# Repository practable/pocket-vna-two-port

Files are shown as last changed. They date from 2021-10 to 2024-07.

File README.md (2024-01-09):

# pocket-vna-two-port

A golang-based web service for the pocketvna.com](https://pocketvna.com/) vector network analyser, with an automated two-port calibration facility provided by additional RF hardware, for use with the open-source [practable.io](https://practable.io] remote lab ecosystem. The user interface is similar to [this](https://github.com/dpreid/pidui), although not yet publically released by the developer (coming soon!)

Status: Prototype has passed measurement quality check, and firmware has been updated to two-ports.

## API

Note that the optional "id" parameter does not affect the command itself, and is provided to help associate replies with the commands that produced them (in case responses come out of order)

### Reasonable range 

```
{"id":"rr","cmd":"rr"}
```
Response:
```
{"id":"rr","t":0,"cmd":"rr","range":{"start":500000,"end":4000000000}}
```

### Calibration

To Perform a full 2-port calibration issue a command like this:

```
{"id":"rcal","t":0,"cmd":"rc","range":{"start":1000000,"end":4000000000},"size":501,"islog":false,"avg":1}
```

501 points is quite slow, so for quick checking functionality, try fewer points.
```
{"id":"rcal","t":0,"cmd":"rc","range":{"start":1000000,"end":4000000000},"size":5,"islog":false,"avg":1}
```

 The `range`, `size`, `isLog` and `avg` are the same as before. This example uses the largest scan size possible (501 points)

### Measurement

These are all the measurements that can be taken (as before, they use the size, and range parameters from the cal):

```
{"id":"short","t":0,"cmd":"crq","what":"short","avg":1,"sparam":{"s11":true,"s12":true, "s21":true,"s22":true}}
{"id":"open","t":0,"cmd":"crq","what":"open","avg":1,"sparam":{"s11":true,"s12":true,"s21":true,"s22":true}}
{"id":"load","t":0,"cmd":"crq","what":"load","avg":1,"sparam":{"s11":true,"s12":true,"s21":true,"s22":true}}
{"id":"thru","t":0,"cmd":"crq","what":"thru","avg":1,"sparam":{"s11":true,"s12":true,"s21":true,"s22":true}}
{"id":"dut1","t":0,"cmd":"crq","what":"dut1","avg":1,"sparam":{"s11":true,"s12":true,"s21":true,"s22":true}}
{"id":"dut2","t":0,"cmd":"crq","what":"dut2","avg":1,"sparam":{"s11":true,"s12":true,"s21":true,"s22":true}}
{"id":"dut3","t":0,"cmd":"crq","what":"dut3","avg":1,"sparam":{"s11":true,"s12":true,"s21":true,"s22":true}}
{"id":"dut4","t":0,"cmd":"crq","what":"dut4","avg":1,"sparam":{"s11":true,"s12":true,"s21":true,"s22":true}} 
```

### Step wise calibration

New feature added to support students learning about the cal process

SC Command (Setup cal, sets the frequency range, number of points, distribution type, and averaging count)
`{"cmd":"sc","range":{"start":1000000,"end":4000000000},"size":20,"islog":false,"avg":1}`

SC Response
```
{"message":"ok","Command":{"id":"","t":0,"cmd":"sc","range":{"start":1000000,"end":4000000000},"size":20,"islog":false,"avg":1,"sparam":{"s11":false,"s12":false,"s21":false,"s22":false},"result":null,"what":"thru"}}
```

MC Short Command:
`{"cmd":"mc","what":"short"}`

MC Short Response (has no data):
```
{"message":"ok","Command":{"id":"","t":0,"cmd":"mc","range":{"start":0,"end":0},"size":0,"islog":false,"avg":0,"sparam":{"s11":false,"s12":false,"s21":false,"s22":false},"result":null,"what":"short"}}
```

MC Open Command:
`{"cmd":"mc","what":"open"}`

MC Open Response (has no data):
```
{"message":"ok","Command":{"id":"","t":0,"cmd":"mc","range":{"start":0,"end":0},"size":0,"islog":false,"avg":0,"sparam":{"s11":false,"s12":false,"s21":false,"s22":false},"result":null,"what":"open"}}
```

MC Load Command:
`{"cmd":"mc","what":"load"}`

MC Load Response (has no data):
```
{"message":"ok","Command":{"id":"","t":0,"cmd":"mc","range":{"start":0,"end":0},"size":0,"islog":false,"avg":0,"sparam":{"s11":false,"s12":false,"s21":false,"s22":false},"result":null,"what":"load"}}
```

MC Thru Command:

`{"cmd":"mc","what":"thru"}`

MC Thru Response (has no data):

```
{"message":"ok","Command":{"id":"","t":0,"cmd":"mc","range":{"start":0,"end":0},"size":0,"islog":false,"avg":0,"sparam":{"s11":false,"s12":false,"s21":false,"s22":false},"result":null,"what":"thru"}}
```

CC Command (cal confirm):

`{"cmd":"cc"}`

CC Command (has data, "what" indicates this is data for the thru with cal applied)
```
{"id":"","t":0,"cmd":"cc","range":{"start":0,"end":0},"size":0,"islog":false,"avg":0,"sparam":{"s11":false,"s12":false,"s21":false,"s22":false},"result":[{"s11":{"real":6.798285684431499e-16,"imag":2.4445757591977986e-15},"s12":{"real":1.0000000000000038,"imag":3.961372257700955e-15},"s21":{"real":0.9999999999999997,"imag":-2.5403542658420376e-15},"s22":{"real":-1.3100837207899224e-16,"imag":1.006857580582699e-15},"freq":1000000},{"s11":{"real":-5.4796192872464335e-18,"imag":3.681361022427108e-16},"s12":{"real":0.9999999999999998,"imag":1.291216167493111e-16},"s21":{"real":0.9999999999999998,"imag":1.0329729339944889e-16},"s22":{"real":-5.483483876630498e-16,"imag":2.274972688902102e-16},"freq":211473684},{"s11":{"real":4.935662660074536e-16,"imag":-7.96132869667085e-17},"s12":{"real":1.0000000000000002,"imag":9.417544964280893e-18},"s21":{"real":1,"imag":3.3389477600632256e-17},"s22":{"real":-5.493611090297354e-17,"imag":2.7110250401774997e-17},"freq":421947368},{"s11":{"real":-3.7997788415861466e-16,"imag":-5.874815142871674e-16},"s12":{"real":0.9999999999999998,"imag":-1.3589387524604561e-17},"s21":{"real":1,"imag":1.358938752460456e-16},"s22":{"real":2.7701351888980784e-16,"imag":2.4761558453947516e-16},"freq":632421052},{"s11":{"real":-1.770339245638541e-16,"imag":1.9778244425109326e-16},"s12":{"real":1,"imag":-8.300789127383292e-17},"s21":{"real":1,"imag":-1.3834648545638821e-17},"s22":{"real":1.8971165707760076e-16,"imag":2.4057070110192795e-16},"freq":842894736},{"s11":{"real":-4.2721621505142654e-16,"imag":-3.6944203527273236e-16},"s12":{"real":1.0000000000000002,"imag":1.0316557900882054e-16},"s21":{"real":1,"imag":2.3212255276984624e-16},"s22":{"real":1.4673180020770904e-16,"imag":-7.563249442097559e-17},"freq":1053368421},{"s11":{"real":-7.434581424175234e-17,"imag":-1.9738283167151276e-16},"s12":{"real":1.0000000000000007,"imag":2.653377447265651e-16},"s21":{"real":1,"imag":1.3668914122277596e-16},"s22":{"real":-2.3401087672749595e-16,"imag":1.0842732839585657e-15},"freq":1263842105},{"s11":{"real":3.6225925572304583e-16,"imag":-6.553331226630913e-16},"s12":{"real":1.0000000000000002,"imag":-7.697793525240971e-18},"s21":{"real":1,"imag":-2.232360122319882e-16},"s22":{"real":-1.664758573382055e-16,"imag":4.426697324102885e-16},"freq":1474315789},{"s11":{"real":-2.1111596138986894e-16,"imag":-3.374000478864848e-16},"s12":{"real":0.9999999999999998,"imag":2.500148396700068e-16},"s21":{"real":0.9999999999999997,"imag":1.388971331500038e-16},"s22":{"real":-9.217893404457907e-16,"imag":5.883978158950974e-16},"freq":1684789473},{"s11":{"real":-9.143566579079719e-17,"imag":-1.211669953147277e-16},"s12":{"real":0.9999999999999994,"imag":-3.384880863400854e-16},"s21":{"real":0.9999999999999997,"imag":-1.9131935314874394e-16},"s22":{"real":7.370339974993562e-16,"imag":-8.28234587808332e-16},"freq":1895263157},{"s11":{"real":6.457509151560786e-16,"imag":3.8407024419460014e-16},"s12":{"real":1,"imag":1.9729520543081967e-16},"s21":{"real":1,"imag":1.1097855305483607e-16},"s22":{"real":6.60122631708177e-16,"imag":1.3745123740607558e-16},"freq":2105736842},{"s11":{"real":-3.3440705904509994e-17,"imag":4.449237964595957e-17},"s12":{"real":1.0000000000000002,"imag":-2.5977695183489855e-17},"s21":{"real":1,"imag":-2.5977695183489855e-17},"s22":{"real":-5.030390119684563e-17,"imag":2.0588438761762348e-16},"freq":2316210526},{"s11":{"real":9.761453389683951e-16,"imag":9.948440742403095e-16},"s12":{"real":1,"imag":3.198724411505024e-18},"s21":{"real":1,"imag":-6.173538114204697e-16},"s22":{"real":-5.60392729997236e-16,"imag":1.011513121527802e-15},"freq":2526684210},{"s11":{"real":3.4281792534273156e-16,"imag":1.8971075667988323e-16},"s12":{"real":0.9999999999999998,"imag":1.1750683925917896e-16},"s21":{"real":1.0000000000000002,"imag":-4.0090568688425766e-16},"s22":{"real":-4.803256717402525e-16,"imag":-1.6853048357543685e-16},"freq":2737157894},{"s11":{"real":7.0222190594856e-16,"imag":8.55812317471566e-16},"s12":{"real":0.9999999999999988,"imag":-1.1169563182435168e-15},"s21":{"real":0.9999999999999999,"imag":9.307969318695973e-17},"s22":{"real":1.2657248559624003e-15,"imag":-4.1238155967451286e-16},"freq":2947631578},{"s11":{"real":3.858821128617499e-16,"imag":-5.908283352150228e-16},"s12":{"real":1.0000000000000004,"imag":2.7559016913199073e-16},"s21":{"real":0.9999999999999999,"imag":-3.1910440636335773e-16},"s22":{"real":-8.995649578270255e-16,"imag":1.3676784350870345e-15},"freq":3158105263},{"s11":{"real":2.1930623628836212e-15,"imag":-4.471183287954572e-16},"s12":{"real":1.0000000000000007,"imag":6.624851261896299e-17},"s21":{"real":1.0000000000000009,"imag":-1.5568400465456302e-15},"s22":{"real":-3.910813152158192e-16,"imag":1.497689622024306e-16},"freq":3368578947},{"s11":{"real":-2.146668654496036e-15,"imag":-1.183624872561583e-15},"s12":{"real":1.0000000000000009,"imag":8.946818283441143e-16},"s21":{"real":0.9999999999999997,"imag":7.437272811749428e-16},"s22":{"real":-7.642394840158961e-16,"imag":1.3994328139316487e-15},"freq":3579052631},{"s11":{"real":2.7529090287958957e-17,"imag":7.844753059553777e-16},"s12":{"real":1.0000000000000007,"imag":4.241877296255027e-16},"s21":{"real":1.0000000000000007,"imag":-1.4812904844065175e-16},"s22":{"real":1.4749059628833424e-17,"imag":7.703227823525666e-16},"freq":3789526315},{"s11":{"real":2.1613952847620654e-15,"imag":-1.4106120953151985e-15},"s12":{"real":1.0000000000000018,"imag":1.8138127619939417e-16},"s21":{"real":0.9999999999999996,"imag":-5.654828022686995e-16},"s22":{"real":8.233651548249787e-16,"imag":1.6094852797772485e-15},"freq":4000000000}],"what":"thru"}
```

 If you try to confirm the cal or take a measurement before completing the cal, then you will get an error message, e.g. sending cc before doing anything else ...
 
```
{"message":"not calibrated yet","Command":{"id":"","t":0,"cmd":"cc","range":{"start":0,"end":0},"size":0,"islog":false,"avg":0,"sparam":{"s11":false,"s12":false,"s21":false,"s22":false},"result":null,"what":""}}
```

 If you have started but not finished the cal, then there will be a hint about what is missing. It's not very sophisticated, it checks for short, open, load thru in that order but it is ok to do the measurements in any order. E.g. if you have only done the `sc` and then `mc` for the `short`, and then try `cc`, you get
```
{"message":"calibration not complete (missing open, maybe others)","Command":{"id":"","t":0,"cmd":"cc","range":{"start":0,"end":0},"size":0,"islog":false,"avg":0,"sparam":{"s11":false,"s12":false,"s21":false,"s22":false},"result":null,"what":""}}
```
But if you try a crq, you don't; get any hints, just a message it is not calibrated yet:

CRQ command

```
{"id":"short","t":0,"cmd":"crq","what":"short","avg":1,"sparam":{"s11":true,"s12":true, "s21":true,"s22":true}}
```

CRQ response

```
{"message":"not calibrated yet","Command":{"id":"short","t":0,"cmd":"crq","what":"short","avg":1,"sparam":{"s11":true,"s12":true,"s21":true,"s22":true},"result":null}}
```

### Trying it out

use the dev-debug because it has been modified to display the data stream more conveniently

request rr:
```
{"id":"rr","t":0,"cmd":"rr","range":{"start":500000,"end":4000000000}}
```
response
```
{"id":"rcal","t":0,"cmd":"rc","range":{"start":1000000,"end":4000000000},"size":501,"islog":false,"avg":1}
```

request cal
```
{"id":"rcal","t":0,"cmd":"rc","range":{"start":1000000,"end":4000000000},"size":3,"islog":false,"avg":1}
```
response
```
{"id":"rcal","t":0,"cmd":"rc","range":{"start":1000000,"end":4000000000},"size":3,"islog":false,"avg":1,"sparam":{"s11":false,"s12":false,"s21":false,"s22":false},"result":[{"s11":{"real":-0.00002794712781906128,"imag":-0.0002553611993789673},"s12":{"real":0.00004700571298599243,"imag":0.000007621943950653076},"s21":{"real":0.00005336105823516846,"imag":-0.000005081295967102051},"s22":{"real":0.000048279762268066406,"imag":-0.00021597743034362793},"freq":1000000},{"s11":{"real":-0.0000025406479835510254,"imag":-0.0002896711230278015},"s12":{"real":0.0015550479292869568,"imag":-0.00180024653673172},"s21":{"real":-0.0020975321531295776,"imag":0.001013830304145813},"s22":{"real":-0.0018929839134216309,"imag":0.0009096488356590271},"freq":2000500000},{"s11":{"real":0.002163603901863098,"imag":-0.008152559399604797},"s12":{"real":0.0015474259853363037,"imag":-0.0013009533286094666},"s21":{"real":0.0024291202425956726,"imag":0.0006962120532989502},"s22":{"real":0.0027683377265930176,"imag":-0.006796970963478088},"freq":4000000000}],"what":""}
```

request measurement
```
{"id":"dut1","t":0,"cmd":"crq","what":"dut1","avg":1,"sparam":{"s11":true,"s12":true,"s21":true,"s22":true}}
```
response
```
{"id":"dut1","t":0,"cmd":"crq","what":"dut1","avg":1,"sparam":{"s11":true,"s12":true,"s21":true,"s22":true},"result":[{"s11":{"real":0.7213804056329582,"imag":1.4104697588145223},"s12":{"real":-0.6894871206139953,"imag":0.2700840697023531},"s21":{"real":0.7031091027298517,"imag":0.47775336746611247},"s22":{"real":0.10341030075671172,"imag":0.3654223580872504},"freq":1000000},{"s11":{"real":-0.21755274620868625,"imag":-0.3754279747150785},"s12":{"real":0.6896210346136951,"imag":-0.12124783800081158},"s21":{"real":0.5913287788642378,"imag":-0.17444370058172678},"s22":{"real":-0.19807969221279273,"imag":-0.3255108569280837},"freq":2000500000},{"s11":{"real":-0.6383708479867005,"imag":-0.14863376649864046},"s12":{"real":0.29690952420750577,"imag":-0.0448141195835949},"s21":{"real":0.32891032123190567,"imag":0.003536763868706301},"s22":{"real":-0.4513970279816097,"imag":-0.14868940500662153},"freq":4000000000}]}
```

## Two port set up

## Pin connections

| Pin | Connection      |
|-----|-----------------|
| 2   | Switch Power    |
| 3   | Switch Power    |
| 4   | Port 2 Switch A |
| 5   | Port 2 Switch B |
| 6   | Port 2 Switch C |
| 8   | Port 1 Switch A |
| 9   | Port 1 Switch B |
| 10  | Port 1 Switch C |
| 15  | Port 2 LED      |
| 16  | Port 1 LED      |

## Switch Configuration

The states available in the prototype firmware were:

| State       | P1-A (D8) | P1-B (D9) | P1-C (D10) | P2-A (D4) | P2-B (D5) | P2-C (D6) |
|-------------|-----------|-----------|------------|-----------|-----------|-----------|
| P1 Short    | 0         | 0         | 1          | X         | X         | X         |
| P1 Open     | 0         | 1         | 0          | X         | X         | X         |
| P1 Load     | 0         | 1         | 1          | X         | X         | X         |
| P2 Short    | X         | X         | X          | 1         | 0         | 0         |
| P2 Open     | X         | X         | X          | 1         | 0         | 1         |
| P2 Load     | X         | X         | X          | 1         | 1         | 0         |
| Thru        | 1         | 0         | 0          | 0         | 1         | 1         |
| DUT-1 (5-2) | 1         | 0         | 1          | 0         | 1         | 0         |
| Ch0 P2      | X         | X         | X          | 0         | 0         | 0         |
| Ch1 P2      | X         | X         | X          | 0         | 0         | 1         |
| Ch7 P2      | X         | X         | X          | 1         | 1         | 1         |
| Ch0 P1      | 0         | 0         | 0          | X         | X         | X         |
| Ch6 P1      | 1         | 1         | 0          | X         | X         | X         |
| Ch7 P1      | 1         | 1         | 1          | X         | X         | X         |
| DUT-2 (6-1) | 1         | 1         | 0          | 0         | 0         | 1         |
| DUT-3 (7-0) | 1         | 1         | 1          | 0         | 0         | 0         |
| DUT-4 (0-7) | 0         | 0         | 0          | 1         | 1         | 1         |

The revised, minimal states are:

| State       | P1-A (D8) | P1-B (D9) | P1-C (D10) | P2-A (D4) | P2-B (D5) | P2-C (D6) |
|-------------|-----------|-----------|------------|-----------|-----------|-----------|
| P1 Short    | 0         | 0         | 1          | X         | X         | X         |
| P1 Open     | 0         | 1         | 0          | X         | X         | X         |
| P1 Load     | 0         | 1         | 1          | X         | X         | X         |
| P2 Short    | X         | X         | X          | 1         | 0         | 0         |
| P2 Open     | X         | X         | X          | 1         | 0         | 1         |
| P2 Load     | X         | X         | X          | 1         | 1         | 0         |
| Thru        | 1         | 0         | 0          | 0         | 1         | 1         |
| DUT-1       | 1         | 0         | 1          | 0         | 1         | 0         |
| DUT-2       | 1         | 1         | 0          | 0         | 0         | 1         |
| DUT-3       | 1         | 1         | 1          | 0         | 0         | 0         |
| DUT-4       | 0         | 0         | 0          | 1         | 1         | 1         |

Or in decimal

| State       | P1        | P2        | 
|-------------|-----------|-----------|
| Short       | 1         | 4         |
| Open        | 2         | 5         |
| Load        | 3         | 6         |
| Thru        | 4         | 3         |
| DUT-1       | 5         | 2         |
| DUT-2       | 6         | 1         |
| DUT-3       | 7         | 0         |
| DUT-4       | 0         | 7         |

This table implies the following connections:

### Port 1

| Channel   | Connection |
|-----------|------------|
| RF1       | DUT-4      |
| RF2       | Short      |
| RF3       | Open       |
| RF4       | Load       |
| RF5       | Thru       |
| RF6       | DUT-1      |
| RF7       | DUT-2      |
| RF8       | DUT-3      |

### Port 2

| Channel   | Connection |
|-----------|------------|
| RF1       | DUT-3      |
| RF2       | DUT-2      |
| RF3       | DUT-1      |
| RF4       | Thru       |
| RF5       | Short      |
| RF6       | Open       |
| RF7       | Load       |
| RF8       | DUT-4      |

These connections tally with the prototype.

Note that the connection on the HM321 RF chip on the datasheet.

### Current DUT Setup

The prototype as at 2023-03-02 is set up as follows:

| DUT | Type           | Port/Switch 1 | Port/Switch 2 | 
|-----|----------------|---------------|---------------|
| 1   | 2-Port Filter  | P1            | P2            |
| 2   | 4-Port Coupler | P1            | P4            | 
| 3   | 4-Port Coupler | P1            | P2            |
| 4   | 4-Port Coupler | P1            | P3            |

The 4-Port couplers are all the same, but with different port connections, to allow all four ports to be measured (albeit not as completely as a four-port VNA).

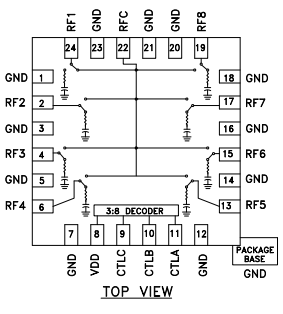
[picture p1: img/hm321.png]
hm321


## Current results

Set debug=true to get a table showing the outputs

```
        P1      P2     P1  P2
short: 1 0 0   0 0 1   1   4
open : 0 1 0   1 0 1   2   5
load : 1 1 0   0 1 1   3   6
thru : 0 0 1   1 1 0   4   3
dut1 : 1 0 1   0 1 0   5   2
dut2 : 0 1 1   1 0 0   6   1
dut3 : 1 1 1   0 0 0   7   0
dut4 : 0 0 0   1 1 1   0   7
```

## Developers

This section contains notes for developers. The code was refactored during 2023 to account for a bug that required two measurements to be taken in a row before the correct DUT was measured. 

### Measurements

A typical user request is for a calibrated measurement of a particular device under test (DUT).

 The `pkg/middle` receives that request over a websocket connection implemented by `pkg/stream`. Upon startup, the firmware makes a local connection to a `relay host` that is in turn connected to the `relay server` instance running in the cloud, that is turn connected to the user.

`pkg/middle` must take a number of measurements, both of cal standards and the DUT, then request a calibration calculation. Measurements require the RF switch to be set to connect the VNA to the right DUT or cal standard.

The `pkg/measure` package combines an RF switch (`pkg/rfusb`) and VNA instance (`pkg/pocket`) together so that it is straightforward to request a particular measurement. 

Once all the required measurements are taken (SOLT + DUT), then using the method shown in `pkg/calibrate`, the gRPC client in `pkjg/pb` is used to request the calibration from our local calibration server - see `py/server.py`. This needs to run locally to the firware because gRPC is HTTP/2 and that is not proxied by the cloud frontends available to us at present. The code in `pkg/pb` is autogenerated protocol buffer code.

```mermaid
 erDiagram
    USER }o--o{ CALIBRATED_MEASUREMENT : requests
    CALIBRATED_MEASUREMENT {
        string port
        array frequencyRange
        result  CalibratedSParametersDUT
    }
    CALIBRATED_MEASUREMENT ||--|| CALIBRATION : requires
        CALIBRATION {
            SParameters short
            SParameters open
            SParameters load
            SParameters thru
            SParameters DUT

        }
     CALIBRATION ||--|{ MEASUREMENT : requires
        MEASUREMENT {
                 string port
        }
    MEASUREMENT ||--|| HARDWARE : requires
        HARDWARE{
        pointer switch
            pointer VNA
        }    
```

TODO 

0. `middle` update hardware test to cycle through all dut at least twice, and then a third time in a different order
1. `middle` Use new direct switch connection in middle
2. `middle` Use new grpc connection in middle

### Golang files

The golang packages are in `./pkg`

If adding new subpackages, then update the reference to the project to the current branch, e.g. after adding the package `pb` to the `fix` branch, `go mod` couldn't find it `@latest` so it needed to be "upgraded" to look at the fix branch. Warning - after pulling to main, update to point to @latest again
```
go get -v -u github.com/practable/pocket-vna-two-port/pkg/pb@fix
go mod tidy
```
### Architecture

The RF Switch is connected directly rather than via `socat`+`websocat` as in the previous generation. This simplifies the configuration of the single board computer and avoids switch commands getting out of sequence on a channel.

The calibration is via gRPC call, again to avoid responses getting out of sequence over a channel. Note that gRPC uses HTTP/2 so we are probably stuck with running this locally on a container

### Building

### Testing

## Overview from the one-port repo

These notes should aid in understanding the ansible scripts in `./sbc`, even though some details differ. Note that the below information has NOT been edited to match changes in the current repo, so differs in the detail e.g. of calibration commands (now two-port), and S-parameter settings in the measurement commands. See commands above for the current version.

This repo contains code and design files for the key parts of the system.

- golang wrapper for the pocket-vna
- golang middleware and clients for the rf-switch and calibration services 
- python calibration service using scikit-rf & websocket libraries
- docker containerisation of the python calibration service
- C/C++ firmware for an arduino nano microcontroller
-
The largest part of this repo is the golang executable `vna` which sequences tasks between the four major parts: 
- user (via websocket service, routed through session host from the external practable.io ecosystem)
- vector network analyser (via golang-wrapped shared C library; local USB connection to hardware)
- rf switch controller (via websocket service, routed through session host; local USB connection to hardware)
- calibration service (via websocket service, routed through session host; runs on local docker container)

`vna` also supplies a `unlock` command to free up any pocketVNA connected to the computer. It is assumed that you only have one VNA per computer (it's possible to support more, and to choose explicitly, but that is not implemented. Our use case is one VNA per host computer,  and we want to auto-discover the VNA).

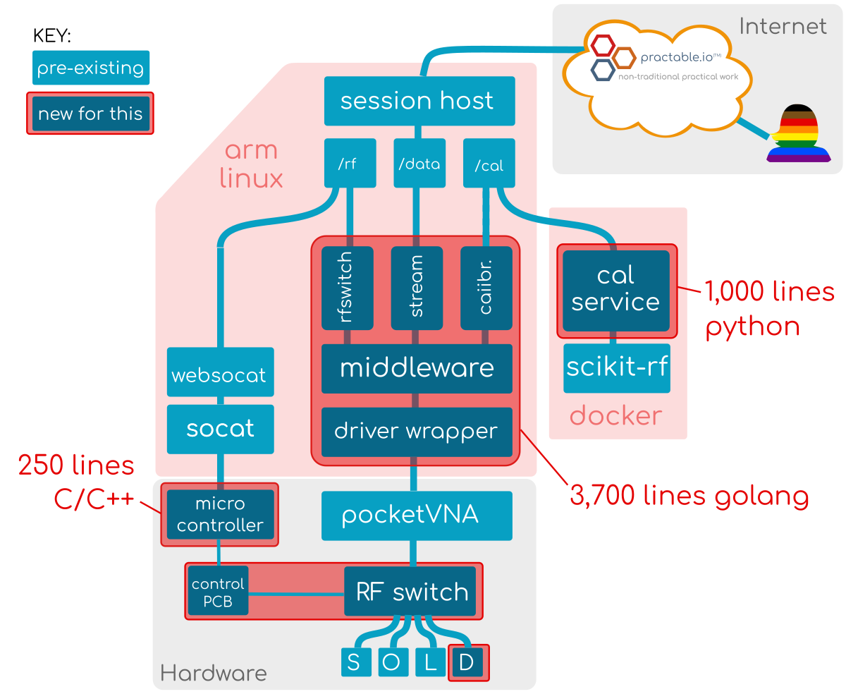
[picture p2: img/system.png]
system


For example, in order to perform a calibration, the golang code does the following tasks

- set the RF switch to the short cal standard
- scan the short, and store the data
- set the RF switch to the open cal standard
- scan the open, and store the data
- set the RF switch to the load cal standard
- scan the load, and store the data
- check all the data are of the correct length

To supply calibrated scans, the golang code does the following

- set the RF switch to the device under test (or whichever cal standard the user is interested in scanning)
- scan the device under test with the same parameters for which we have cal-standard data
- combine the dut data with the cal standard data, and send to the calibration service
- receive the results, re-format the data, and send it to the user

There is a <100ms performance overhead in sending the cal data to the calibration service each time, but this is much smaller than the scan times (tens of seconds), and avoids duplicating state (such as knowledge of what frequency points are being used, and when the cal standards were last scanned).

## Future expansion

Our preferred languages for each of the different parts of the system spanned golang, C/C++ and python. Instead of trying to tightly integrate them or duplicate functionality in one or the other, the JSON-over-websockets communication method was used to separate out concerns, facilitate testing, and allow replacing the RF switch circuit to support two-port cal, add extra calibration methods, and upgrade the API offered to the user to support the extra hardware.

## Installation 

This can be a bit finicky because the pocketVNA library has different name and requirements for different targets, and is only available as compiled source so cannot be automatically built for your target. The manufacturers support a number of major operating systems and platforms, so you should be ok. This code has been tested on amd64/linux and arm/linux.

### vna install 

The core of this repo is the `vna` executable.

0. Download this repo (`git clone git@github.com:timdrysdale/go-pocketvna.git`)
0. replace pkg/pocket/libPocketAPI.so with the appropriate pocketVNA library for your target
0. copy that library to your system path, e.g. for linux /usr/lib (for linux amd64/arm, add `.0` so the ending is `...so.0`)
0. get all dependencies `go get -u ./...' (you may need to add or remove the -lm flag for linking the maths library - not needed on linux 64 bit but needed on Raspbian buster
0. Compile the vna command (`go mod init github.com/timdrysdale/go-pocketvna && cd cmd/vna && go build`)
0. copy the `vna` executable to your usual location on the path (`go install` or do by hand)
0. check it is installed by trying `vna stream --help`

```
vna stream --help
Stream connects the first available pocketVNA to a websocket server. The websocket server is specified via an environment variable

export VNA_DESTINATION=ws://localhost:8888/ws/vna
export VNA_CALIBRATION=ws://localhost:8888/ws/calibration
export VNA_RFSWITCH=ws://localhost:8888/ws/rfswitch

vna stream 

Note that development can be enabled by setting environment variable VNA_DEVELOPMENT
export VNA_DEVELOPMENT=true

Usage:
  vna stream [flags]

Flags:
  -h, --help   help for stream
```

### session install

Install `session` from [practable.io](https://github.com/practable/relay)

If you are using the experiment remotely, you should configure a script to set the forwarding rules at start up (your practable.io admin contact will have details of the tokens etc your experiment needs)

session-rules
```
#!/bin/sh
dataTokenFile="/etc/practable/data.token"
dataAccessFile="/etc/practable/data.access"

dataToken=$(cat "$dataTokenFile")
dataAccess=$(cat "$dataAccessFile")

curl -X POST -H "Content-Type: application/json" -d '{"stream":"data","destination":"'"${dataAccess}"'","id":"1","token":"'"${dataToken}"'"}' http://localhost:8888/api/destinations 
```
This script can be run at start up by enabling a systemd service. The service file is in [services](./ansible/services)

### Docker install

Python is often used for system tasks, so we run our calibration service in a docker container to avoid any version and dependency conflicts.

The steps to manually install Docker are:

```
sudo apt update
# optional:
# sudo apt-upgrade && sudo reboot
curl -fsSL https://get.docker.com -o get-docker.sh
chmod +x ./get-docker.sh
sudo ./get-docker.sh

# for non-privileged use
dockerd-rootless-setuptool.sh install
#check you have docker running
docker version 
#sudo usermod -aG docker $(whoami) #this not be needed -
sudo chmod 666 /var/run/docker.sock #avoid permission denied
#sudo reboot #let all the changes take effect
#<wait for reboot>
```

Build and start the docker image (use tmux if you are ssh'ing into your rpi, so you can have extra terminals open)
```
export platform=linux-amd64  #or linux-arm32v7
cd py/docker/app-${platform}
./build.sh && ./start.sh
```

You can check the calibration service is up and running by connecting to it with `websocat`

```
$ websocat ws://localhost:8888/ws/calibration -
```

Calibration commands are usually quite long, so here is one with just a single data point
```
{"cmd": "oneport", "freq": [1000000.0], "short": {"real": [0.9166423490437918], "imag": [0.65760561459272446]}, "open": {"real": [0.8574903206586918], "imag": [0.43502949254752743]}, "load": {"real": [0.3002840906307519], "imag": [0.297151596182326]}, "dut": {"real": [0.4975782258013943], "imag": [0.4293572766329692]}}
```
which will return a response like this:

```
{"freq": [1000000.0], "S11": {"Real": 0.032134147957021554, "Imag": 0.0984021118681623}}
```

## vna setup
 
The usage / setup is mostly the same for a local system running on a desktop for testing, or deployed on a raspberry pi for remote access. The remote system tends to have everything autostart on boot, and include some setup to make a connection to the `practable.io` infrastructure servers. This is added complication that you do not need, and may not want, if working on a desktop. Starting the services manually is fine. Start `session host` first, then `websocat`, then you can start `socat`, `vna stream` and the `docker` calibration service in any order. The system will only supply calibrated data when the rfswitch and calibration services are running.

It is recommended to try unlocking the devices first - just in case the service is restarting and the pocketVNA was locked by the previous instance

The websocket connections between services are specified by environment variables, so that `vna stream` knows where to find them. The `session host` does not mind which particular endpoints are used - but the endpoints must be set the same for `vna stream` and the service that it is connecting to. The full instantiation of the [practable.io](https://practable.io) services on the host computer (usually a raspberry pi) are out of the scope of this documentation (early adopters are encouraged to contact us for information on how to obtain support <support@practable.io>).

Assuming your target is already running [relay/sessionhost](https://github.com/timdrysdale/relay) (see `cmd/session`), then you can use the following files to automate the startup of the services you need:

vna-data:
```
#!/bin/bash
export VNA_DESTINATION=ws://localhost:8888/ws/data
export VNA_CALIBRATION=ws://localhost:8888/ws/calibration
export VNA_RFSWITCH=ws://localhost:8888/ws/rfswitch
vna unlock
vna stream
```

socat-rfswitch:
```
#!/bin/sh
socat /dev/ttyUSB0,echo=0,b57600,crnl tcp:127.0.0.1:9999
```

Note you may have to add yourself to the dialout and tty groups.
```
sudo usermod -a -G dialout pi
sudo usermod -a -G tty pi
```

websocat-rfswitch:
```
#!/bin/sh
websocat ws://localhost:8888/ws/rfswitch tcp-listen:127.0.0.1:9999 --text
```

You can check the `rfswitch` is running by 
```
websocat ws://localhost:8888/ws/rfswitch -
```
Issue commands to change the port
```
{"set":"port","to":"open"}
```

should yield a reply of
```
{"report":"port","is":"open"}
```

### Service files

Service files are in <./ansible/services>. Note most are fairly similar, except `socat-data` which must wait long enough that `websocat-data` has started (ca 10s leaves a safe margin in practice).

### Verifying that the services are working

Connect to `vna` over websocket using `websocat`
```
websocat ws://localhost:8888/ws/data -
```
Then send a ReasonableFrequencyRange command
```
{"cmd":"rr"}
```
which should return something like
```
{"id":"","t":0,"cmd":"rr","range":{"start":500000,"end":4000000000}}
```

This confirms that `vna` is up and running, and connected to a pocketVNA.

Now try a command that needs the rfswitch
```
{"cmd":"rc","range":{"start":1000000,"end":4000000000},"size":3,"islog":false,"avg":1,"sparam":{"s11":true,"s12":false,"s21":false,"s22":false}}
```
should return something like:

```
{"id":"","t":0,"cmd":"rc","range":{"start":1000000,"end":4000000000},"size":3,"islog":false,"avg":1,"sparam":{"s11":true,"s12":false,"s21":false,"s22":false},"result":[{"s11":{"real":-0.0007592514157295227,"imag":0.0006944984197616577},"s12":{"real":0,"imag":0},"s21":{"real":0,"imag":0},"s22":{"real":0,"imag":0},"freq":1000000},{"s11":{"real":0.0004634261131286621,"imag":-0.0001447424292564392},"s12":{"real":0,"imag":0},"s21":{"real":0,"imag":0},"s22":{"real":0,"imag":0},"freq":2000500000},{"s11":{"real":0.0024859830737113953,"imag":-0.005337625741958618},"s12":{"real":0,"imag":0},"s21":{"real":0,"imag":0},"s22":{"real":0,"imag":0},"freq":4000000000}]}

```

and a command that needs the calibration service

```
{"cmd":"crq","what":"dut","avg":1,"sparam":{"s11":true,"s12":false,"s21":false,"s22":false}}
```

which should return something like:

```
{"id":"","t":0,"cmd":"crq","what":"dut","avg":1,"sparam":{"s11":true,"s12":false,"s21":false,"s22":false},"result":[{"s11":{"real":1.0031062693348898,"imag":-0.012728241016514735},"s12":{"real":0,"imag":0},"s21":{"real":0,"imag":0},"s22":{"real":0,"imag":0},"freq":1000000},{"s11":{"real":-0.1335237960932827,"imag":-0.09618931729902436},"s12":{"real":0,"imag":0},"s21":{"real":0,"imag":0},"s22":{"real":0,"imag":0},"freq":2000500000},{"s11":{"real":-0.4883905666762738,"imag":-0.13897086282584725},"s12":{"real":0,"imag":0},"s21":{"real":0,"imag":0},"s22":{"real":0,"imag":0},"freq":4000000000}]}
```

## Interface 

There are three commands directly supported by the pocketvna shared library:

0. `rr`: get the reasonable frequency range for the device (useful `proof of connection` command when troubleshooting)
0. `sq`: get S-parameters at a single frequency (uncalibrated)
0. `rq`: get S-paramters at a range of frequencies (uncalibrated)

we add two more commands to support calibration, which are the two main commands we use: 

0. `rc`: do a calibration over a frequency range for a certain number of steps 

0. `crq`: get S-parameters frequencies (calibrated), using whatever frequency points were specified in the last `rc`

There is also a heartbeat sent every second from the driver, to let you know it is still connected. You can use the absence of this heartbeat to infer that your connection has dropped (it is unlikely the driver has stopped, although that is technically possible if there is a power outage). This heartbeat is added because VNA experiments are unlikely to use a camera (and we've been using the video to check for connection drops, so without it we need something else to check).

```
{"cmd":"hb"}
```

In order to relate commands to responses you can include an ID `id` (string) and/or time `t` (int) field.

### rr

Command

```
{"cmd":"rr"}
```

Response

```
{"id":"","t":0,"cmd":"rr","range":{"Start":500000,"End":4000000000}}
```

Start is the lowest frequency (in Hz) that the VNA can operate at, and End is the highest.

### sq

`sq` gets the requested S-parameters at a single frequency. 

The parameters are:

    - freq (in Hz) at which to take the measurement at
	- avg number of times to take the reading (which are then averaged together)
	- sparam select which S-params are needed - the more you select, the longer it takes

Command:

```
{"id":"945102d5-94e4-448e-bbbf-48384c662711","t":1634664795,"cmd":"sq","freq":100000,"avg":1,"sparam":{"S11":true,"S12":false,"S21":true,"S22":false}}
```
Response:

```
{"id":"945102d5-94e4-448e-bbbf-48384c662711","t":1634664795,"cmd":"sq","freq":100000,"avg":1,"sparam":{"S11":true,"S12":false,"S21":true,"S22":false},"result":{"S11":{"Real":0.0001702234148979187,"Imag":0.0005754455924034119},"S12":{"Real":0,"Imag":0},"S21":{"Real":-0.00004191696643829346,"Imag":-0.00012067705392837524},"S22":{"Real":0,"Imag":0}}}
```

### rq

Get the requested S-parameters at a range of frequencies. Parameters:

    - range (start, end) the start and end of the frequency range to take measurements
	- size the number of separate frequency points to measure at, across the range
	- isLog whether to use a log (isLog = true) or linear (isLog = false) distribution
	- avg number of times to take each reading (which are then averaged together)
	- sparam select which S-params are needed - the more you select, the longer it takes

command
```
{"cmd":"rq","range":{"Start":100000,"End":4000000},"size":2,"isLog":true,"avg":1,"sparam":{"S11":true,"S12":false,"S21":true,"S22":false}}
```

response
```
{"id":"","t":0,"cmd":"rq","range":{"Start":100000,"End":4000000},"size":2,"isLog":true,"avg":1,"sparam":{"S11":true,"S12":false,"S21":true,"S22":false},"result":[{"S11":{"Real":0.00013846158981323242,"Imag":0.00027057528495788574},"S12":{"Real":0,"Imag":0},"S21":{"Real":-0.000031754374504089355,"Imag":-0.0002350062131881714},"S22":{"Real":0,"Imag":0}},{"S11":{"Real":0.00470772385597229,"Imag":0.003948085010051727},"S12":{"Real":0,"Imag":0},"S21":{"Real":0.000017777085304260254,"Imag":-0.000005081295967102051},"S22":{"Real":0,"Imag":0}}]}
```

Note that the frequencies are not (currently) included in the response. They can be calculated according to the formulas given in the openAPI library header, which are (@p denotes a parameter, e.g. ```@p start``` means the parameter start)

```
     *  Distributions:
     *    Linear:      (@p start * 1000 + ((@p end - @p start) * 1000 / (@p steps - 1)) * index) / 1000
     *       (Pay Attention: all numbers are integers. Last element is forced to be equalt to @p end)
     *    Logarithmic: (@p from * powf((float)to / from, (float)index / (steps - 1)))
     *       Formula is taken from 10 ** (lg from +  ( lg to - lg from ) * index /  (steps - 1)). 4-bytes float are used
     *       Pay attention: arithmetic is pretty imprecise on a device
	 
```
These frequency points are calculated in this library, because they are not sent from the hardware. Here is a table of 11 points from 1MHz - 500MHz, taken from the native application for Linear and Log scans. Note that these values from the native app are not quite the same as we expect from the formula for the case of a Log distribution, although the precision issue is acknowledged in the library header file from the supplier as if it is a hardware issue but the values are probably calculated in the native app - the differences are quite small and probably not significant.

| Point  | Linear (both)     |  Log (native app)      | Log (go-pocketVNA)      |  delta |
| -------|-------------|------------|-----------|--------|
| 0      |  1000000    | 1000000    | 1000000   |        |
| 1      |  50900000   | 1861646    | 1861646   |        |
| 2      |  100800000  | 3465724    | 3465724   |        |
| 3      |  150700000  | 6451951    | 6451950   |  -1    |
| 4      |  200600000  | 12011245   | 12011244  |  -1    |
| 5      |  250500000  | 22360680   | 22360680  |        |
| 6      |  300400000  | 41627668   | 41627660  |  -8    |
| 7      |  350300000  | 77495944   | 77495949  |  +5    |
| 8      |  400200000  | 144270000  | 144269991 |  -9    |
| 9      |  450100000  | 268579552  | 268579588 | +36    |
| 11     |  500000000  | 500000000  | 500000000 |        |

### rc

This uses the same JSON structure as the `rq` command, but change `"cmd":"rq"` to `"cmd":"rc"` and ensure that `"sparam":{"S11":true,"S12":false,"S21":false,"S22":false}}` because only cal on port one is supported:

```
{"cmd":"rc","range":{"Start":100000,"End":4000000},"size":2,"isLog":true,"avg":1,"sparam":{"S11":true,"S12":false,"S21":false,"S22":false}}
```

The maximum size is 512, and it is conventional to ask for 501 points for a nice even spacing. A calibration for 501 points takes approx 30 seconds.

### crq

This is a subset of the `rq` object, with `"cmd":"crq"`, and ensure that `"sparam":{"S11":true,"S12":false,"S21":false,"S22":false}}`

```
{"cmd":"crq","avg":1,"sparam":{"S11":true,"S12":false,"S21":false,"S22":false}}
```

## Example data

Good data from a passive device under test always returns a gain of less than 0dB (i.e. without power from a bias supply, it can't add any power of its own) so we can see that in the following results, we should not rely on values close to DC (for the calibration we did, at least). Also, there is some drift in this measurement of a cable, bearing in mind the cable was re-connected after the first few scans and the device moved, so not an entirely fair test on the device. This data was collected in the native app and plotted using python's matplotlib.pyplot.

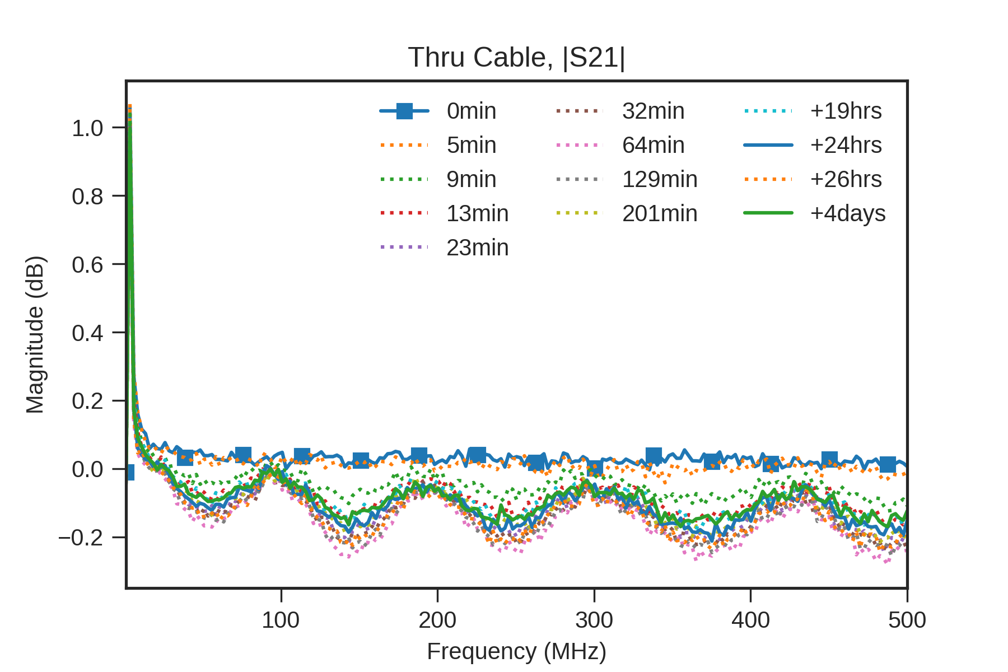
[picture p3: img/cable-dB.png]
magnitude

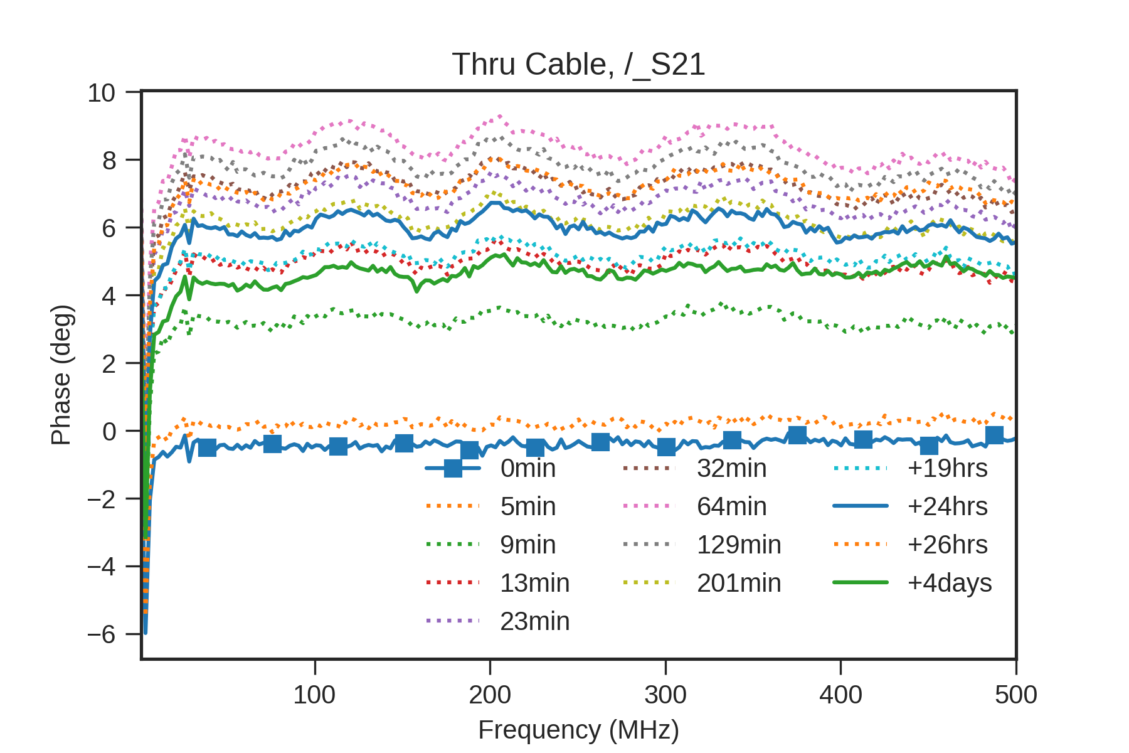
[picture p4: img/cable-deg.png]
phase


### Raw data 

```
{"cmd":"rq","range":{"Start":100000,"End":4000000},"size":201,"isLog":true,"avg":1,"sparam":{"S11":true,"S12":true,"S21":true,"S22":true}}
```

Result returns about 15 sec later, with S-parameters at 201 frequency points:

```
{"id":"","t":0,"cmd":"rq","range":{"Start":100000,"End":4000000},"size":201,"isLog":true,"avg":1,"sparam":{"S11":true,"S12":true,"S21":true,"S22":true},"result":[{"S11":{"Real":0.000034302473068237305,"Imag":0.00037600845098495483},"S12":{"Real":-0.0010073482990264893,"Imag":0.00012448430061340332},"S21":{"Real":-0.0013414323329925537,"Imag":0.0005551204085350037},"S22":{"Real":0.00003937631845474243,"Imag":0.00023628026247024536},"Freq":100000},{"S11":{"Real":0.00006987154483795166,"Imag":0.00010670721530914307},"S12":{"Real":-0.0010479986667633057,"Imag":0.00009654462337493896},"S21":{"Real":-0.0013172999024391174,"Imag":0.0008002892136573792},"S22":{"Real":0.00007876008749008179,"Imag":0.0003162994980812073},"Freq":101862},{"S11":{"Real":0.00014227628707885742,"Imag":0.00035568326711654663},"S12":{"Real":-0.0010594278573989868,"Imag":0.0003429800271987915},"S21":{"Real":-0.0013439729809761047,"Imag":0.0009235069155693054},"S22":{"Real":0.00011432915925979614,"Imag":0.0001664087176322937},"Freq":103758}, ... <snip> ...]}
```

## Developer info

These sections contain some information that may be relevant to developers.

### CGO info

An example of using cgo can be found [here](https://github.com/timhughes/cgoexample) - note you have to delete hello.c from the project directory to avoid `multiple definition of main` error.

There are some differences between C and golang which could create difficulties for users of some C libraries [here](https://docs.yottadb.com/Presentations/DragonsofCGO.pdf), especially where there are:
0. pointers to structs containing other pointers
1. callbacks
2. issues not apparent until garbage collection is triggered

### Performance

It is unclear whether the newer, faster firmware is supported on linux. From the manual:-

```
Pay attention : that newer firmware supports 2 interfaces:
1. HID -- it is universal and easy. Supported by all platforms. But it is slow
2. VCI -- available since firmware V2.10. On Windows requires a special driver (for
example zadig/Interface 1) It is faster. May be unavailable on Mac-OS
In this case both interfaces are listed as individual (separated\independent) items with
the same Serial Number.
It is bad idea to connect both interfaces at the same time and especially bad to perform
scan concurrently
```

Thus to use this newer firmware we will likely need to enumerate devices and handle lists, etc. This should be ok because the types in the C library can be used as parameters.

### Descriptions

Note that getting the first handle will literally just get a handle - you cannot access the description from that handle. If you want the description, you need to get a list of descriptions, and then hask for the handle for the description you like the best. So don't bother trying to access description fields from the handle or handle pointer.

#### Result codes

The result strings are copied from `pocket.h`, primarily to help with debugging by providing some meaning to non-zero error codes. The result from the functions is an C enum, which is only an `int`, so can be typecast back to Go int, then used as the index into an array of strings. For example, If there is no device, then attempting to get a device handle returns code 0x05, or `PVNA_Res_NoDevice` or if a function completes successfully it returns 0x00, which has the string `PVNA_Res_Ok`.

### Testing

The testing for this library assumes the presence of pocketVNA - this avoids mocking the API library and the hardware.

The testing routine issues are force unlock command which should unlock any available pocketVNA. Testing will take place with the first available handle found by the openAPI library. If there is no hardware available you will see:
```
=== RUN   TestGetReleaseHandle
    TestGetReleaseHandle: pocket_test.go:45: 
        	Error Trace:	pocket_test.go:45
        	Error:      	Received unexpected error:
        	            	PVNA_Res_NoDevice
        	Test:       	TestGetReleaseHandle
--- FAIL: TestGetReleaseHandle (0.00s)
```

This probably just means your pocketVNA is unplugged.

If you plug it in and it is working, then you will see the test(s) pass (this output before other tests were added)

```
go build -v && go test -v && go vet
=== RUN   TestGetReleaseHandle
--- PASS: TestGetReleaseHandle (0.06s)
PASS
ok  	_/home/your-path/go-pocketvna/pkg	0.100s
```

#### SingleQuery

Cable disconnected at port 1

```
=== RUN   TestSingleQuery
{(-3.302842378616333e-05-0.00019435584545135498i) (1.2695789337158203e-05-1.9058585166931152e-05i) (-7.614493370056152e-06-2.4139881134033203e-05i) (3.810226917266846e-05-0.00016132742166519165i)}
```

Cable connected

```
{(-0.0013300031423568726+0.000985749065876007i) (0.0026688948273658752-0.005279362201690674i) (0.002047717571258545-0.006369277834892273i) (-0.0012982413172721863+0.0008942857384681702i)}
```

### How to load a touchstone file in python

Install [scikit-rf](https://scikit-rf.readthedocs.io/en/latest/tutorials/Installation.html), usually
```
pip install scikit-rf

```

start a python session, load and plot your file (change to suit your filename)

```
import matplotlib.pyplot as plt
import skrf as rf
load = rf.Network('dut.s1p')
dut.plot_s_db()
plt.savefig('dut_db.png', dpi=300)
plt.close()
dut.plot_s_deg()
plt.savefig('dut_deg.png', dpi=300)
plt.close()
```

### API to the API

since pointers container pointers are difficult to handle, the preferred API is the range API, probably.

## Testability, and future substitution of other hardware ...

There is really only three commands that the user interface needs to know about - GetReasonableFrequencyRange, SingleQuery, RangeQuery.

Therefore a simple remote driver would grab a device handle, and sit back and wait for these commands.

Getting the callback to work would be pretty useful, too, for the rangequery command. Can we poke percentage complete values into a channel?

### Small gotchas with cgo

#### Could not determine type of name error

```
To access a struct, union, or enum type directly, prefix it with struct_, union_, or enum_, as in C.struct_stat.
```
for example
```
C.enum_PocketVNADistribution(distr), //note we have to add enum_ to access this name
```

### Preparing PI image

Use [pishrink](https://github.com/Drewsif/PiShrink)

```
sudo dd if=/dev/sdb of=/home/<user>/rpi-config/vna-cal-2022-01-31.img bs=4M status=progress
sudo pishrink.sh -p vna-cal-2022-01-31.img vna-cal-2022-01-31-shrunk.img
```

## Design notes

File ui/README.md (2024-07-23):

# Pocket VNA 2-port User Interface

Two interfaces are currently available for the pvna-oneport remote lab.

- [default](./default/)
- [graphical](./graphical/)

## default UI

The **default** interface is a single page app with an automated calibration procedure. Users set the number of data points as well as the start and end frequencies for calibration. After calibrating, users have access to four dut measurements: 1 filter and 3 coupler measurements.

Data (magnitude and phase) are plotted on an interactive graph: either plot can be hidden/shown by clicking the corresponding box in the graph legend. Phase can be plotted wrapped (around 180 deg) or unwrapped. Data are also provided in an on-screen table, which supports either real/imag or mag/phase representations, and can be downloaded for external manipulation as a CSV or s2p file. Four separate plots of the scattering parameters are included: s11, s12, s21 and s22.

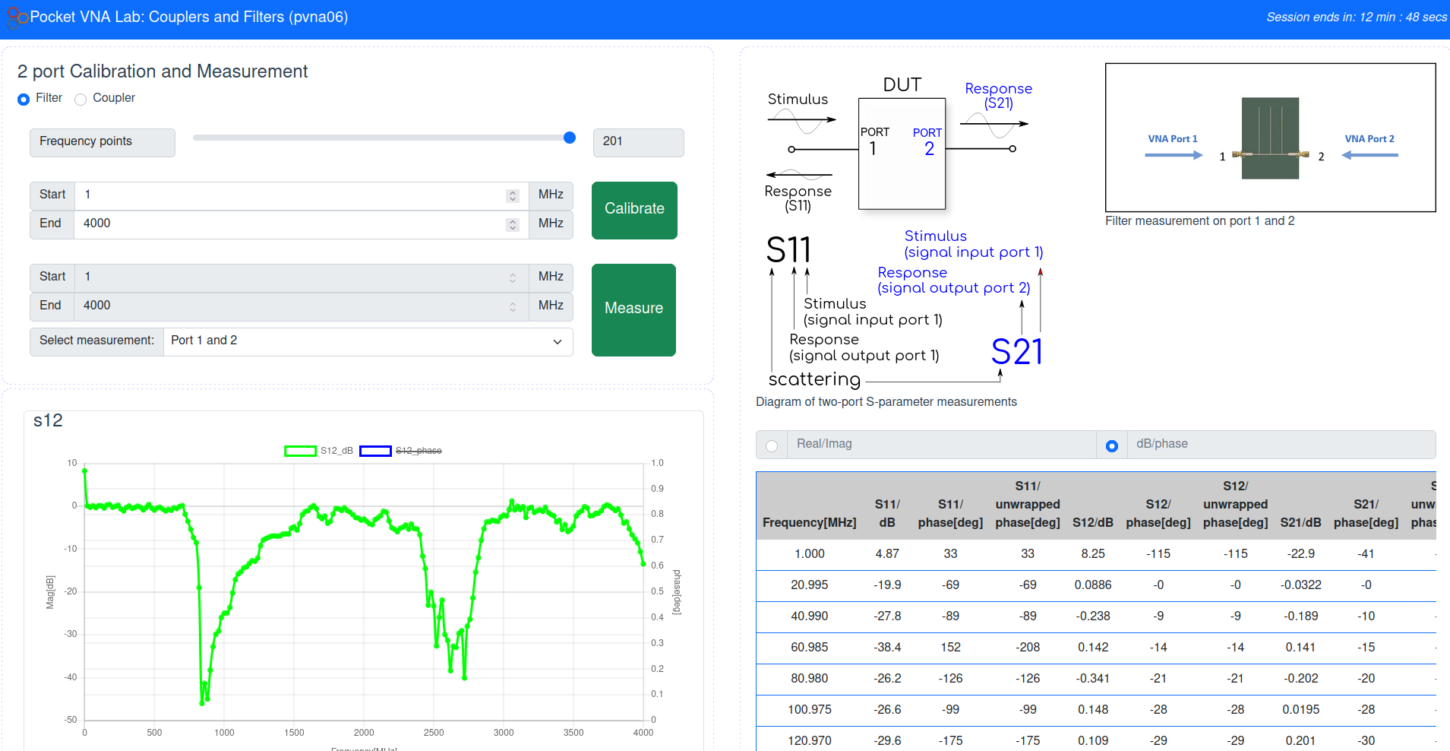
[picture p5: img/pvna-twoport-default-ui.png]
pvna-oneport-default


## graphical UI

The **graphical** user interface is a multi-page app that requires a "manual" calibration procedure. Using the first tab ```1) Set Frequency range```, users set the number of data points and start and end frequencies. Once set, the ``2) Calibration`` tab is used to perform the SOLT calibration procedure: scanning and saving each calibration standard separately before the calibration can be completed. Once calibration is complete the tab turns green and provides access to the ``3) Verification`` tab, where short, open and load measurements can be verified by the user using a smith chart (and standard mag/phase plot). Once verified, the ``4) Measurement`` tab enables measurement of the four available DUTs and display of data using a table, mag/phase plot, smith chart or downloaded for external use.

Parameters set in ```1) Set Frequency range``` will be reflected at subsequent steps without being able to be changed. To update the frequency range or number of data points, return to the first tab. If values are updated here, a re-calibration will be required before any measurements can be taken again.

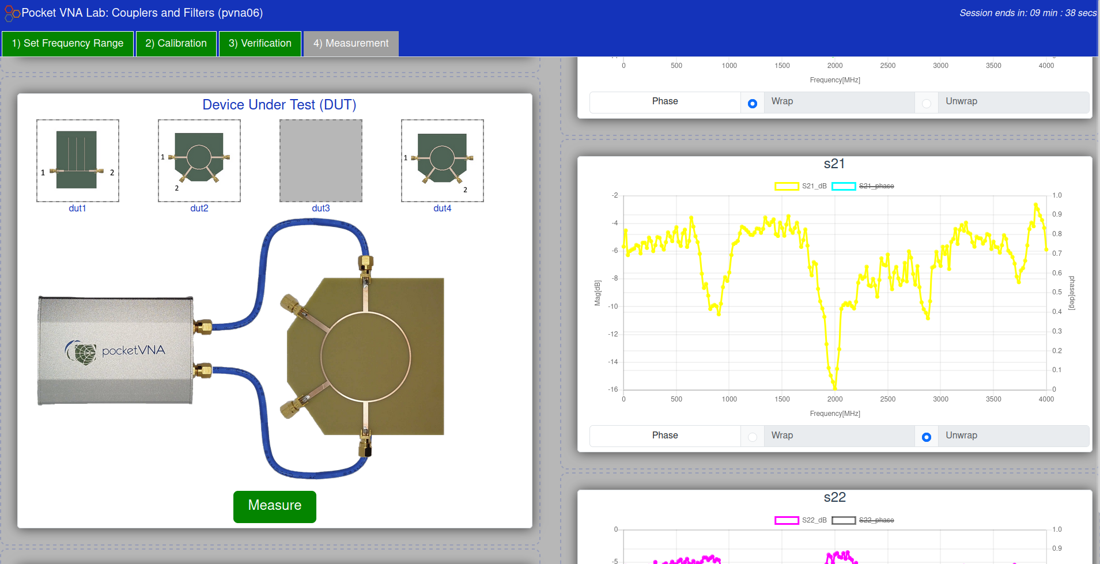
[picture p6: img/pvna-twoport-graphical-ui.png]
pvna-oneport-graphical


## Recommended settings

The number of data points is restricted to between 2 and 201, with the recommendation to using the full 201 data points,

The minimum frequency that the PocketVNA can measure is 0.5 MHz and the maximum recommended frequency is 4000 MHz. Outside of this range, the user interface will highlight an issue with the input frequency with a red box around the input.

## Build procedure

Requirements: ```npm```, all experiments are developed and built using a Linux-based OS.

The practable user interfaces use ```vite``` build tools.

The expected build procedure (not tested from scratch) is as follows:

1) Download the [pocket-vna-two-port](https://github.com/practable/pocket-vna-two-port) repo.
2) Navigate to the appropriate ui in the command line e.g.:

```
cd ~/pocket-vna-two-port/ui/default
```
3) Install all necessary packages from the 'package.json' file: ```npm install```
4) Set the ```VITE_BASE``` in ```.env.production``` to the necessary base path. 
5) Build for development and testing: ```npm run dev```
6) Build for production: ```npm run build``` - the dist folder will contain the built files for deployment

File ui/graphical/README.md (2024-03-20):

# pvna-ui

Copy of 1 port graphical UI - temporary

# Dev notes

For mobile or touchscreen, currently tapping an image during calibration will automatically apply it to port 1 - need to update this to allow either port to be selected

## Project setup
```
npm install
```

### Compiles and hot-reloads for development
```
npm run serve
```

### Compiles and minifies for production
```
npm run build
```

### Lints and fixes files
```
npm run lint
```

### Customize configuration
See [Configuration Reference](https://cli.vuejs.org/config/).

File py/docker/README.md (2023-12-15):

# Docker deployment

## Building an image for the raspberry pi (arm32v7)

This needs to be built on the raspberry pi, due to a lack of suitable emulators for the raspberry pi 4. Some earlier models are available with QEMU but not suitable for this task.

### Docker on Odroid C4

This error below is beacuse the [kernel out of date](https://github.com/docker/cli/issues/4273) in the ubuntu image we're using on the odroids
```
runc run failed: unable to start container process: error during container init: error setting cgroup config for procHooks process: bpf_prog_query(BPF_CGROUP_DEVICE)
```

Fix 1 - upgrade OS to Odroid community Ubuntu image which uses kernel v5.15.
Fix 2 - set systemd.unified_cgroup_hierarchy=0 to bootargs in /media/boot/boot.ini (This worked on pvna10 with Linux odroid 4.9.337-13 #1 SMP PREEMPT Tue Nov 28 16:28:39 UTC 2023 aarch64 aarch64 aarch64 GNU/Linux)

having issues with versions between protoc and the python grpcio version, after breaking change in library

#### Try running directly in python on odroid

python on system is version 3.10

sudo pip install is not recommended but trying it to ensure can run as root

```
sudo pip install grpcio
sudo pip install matplotlib
sudo pip install numpy
sudo pip install scipy
sudo pip install scikit-rf
sudo pip install google-api-python-client
```

allow sudo to use go
```
sudo visudo #add /usr/local/go/bin to the secure_path
```

install protocol buffer compilers into user's own path
```
#sudo go install github.com/golang/protobuf/protoc-gen-go@latest
go install google.golang.org/grpc/cmd/protoc-gen-go-grpc@latest
go install google.golang.org/protobuf/cmd/protoc-gen-go@latest
```

add go to path, by editing `~/.profile`
```
# set PATH so it includes go bin if it exists
if [ -d "$HOME/go/bin" ] ; then
    PATH="$HOME/go/bin:$PATH"
fi
```

Right, libprotoc is ver 3.12 and can't rebuild libprotoc on odroid because package bazel not available via apt-get (could try to build)

alt plan is to downgrade protobuf in python

```
sudo pip install --force-reinstall -v "protobuf==3.20.0"
```

OK, this works, now to sort this in the `requirements.txt`

### Installing Docker on the RPi4

Ensure you are using a raspberry pi with the latest raspbian pi OS lite 32 (currently kernal 5.15)

```
$uname -a
Linux raspberrypi 5.15.84-v7l+ #1613 SMP Thu Jan 5 12:01:26 GMT 2023 armv7l GNU/Linux
```
Update as usual

```
sudo apt update
sudo apt upgrade
```

Install docker....

```
curl -sSL https://get.docker.com | sh
```
avoid needing sudo to run docker commands
```
sudo usermod -aG docker $USER 
```

After installing docker, enable it to start on statup.
```
sudo systemctl enable docker
```

log out, log in and try hello world
```
docker run hello-world 
```

```
#get sources
cd ~
mkdir sources
cd sources
git clone https://github.com/practable/pocket-vna-two-port.git
cd pocket-vna-two-port/py/docker/app-linux-arm32v7 
sudo build #docker throws a permission denied if you try to run it as an unprivileged user
```

The build is quite slow compared to the desktop build - grab a cuppa / go for a walk.
build start 16:28

## Notes from first version

The Docker container for linux/amd64 and linux/arm32v7 differ because of the lack of pre-compiled python packages on the arm32v7 (Raspberry Pi 4) platform.

A <600MB image is created on ubuntu desktop, in a few minutes, with this Dockerfile:
```
FROM python:3.7-slim
ADD calibration.py /
ADD client.py /
ENV WEBSOCKET ws://172.17.0.1:8888/ws/calibration
COPY ./requirements.txt /var/www/requirements.txt
RUN pip install -r /var/www/requirements.txt
CMD [ "python", "./client.py" ]
```

The build is much slower on rpi4 than desktop because the python dependencies are being compiled. A ~1.6GB image is created in several hours with this Dockerfile:

```
# syntax=docker/dockerfile:1
FROM arm32v7/python:3.7-buster AS base
ENV DEBIAN_FRONTEND=noninteractive
RUN apt-get update && apt-get install -y libblas3 liblapack3 liblapack-dev libblas-dev libatlas-base-dev gfortran zlib1g
RUN pip install numpy
RUN pip install scipy
RUN pip install scikit-rf
RUN pip install websocket-client

FROM base AS app
ADD calibration.py /
ADD client.py / 
ENV WEBSOCKET ws://172.17.0.1:8888/ws/calibration
CMD [ "python", "./client.py" ]
```

We use a two-stage build for the raspberry pi to make updates to the python code quicker to deploy, because it avoids the need to recompile any of the python libraries. 

Note: if you just want to build the base image alone, for another project, this Dockerfile will create a layer with the same hash as the `base` layer in the previous dockerfile. 

```
# syntax=docker/dockerfile:1
FROM arm32v7/python:3.7-buster
ENV DEBIAN_FRONTEND=noninteractive
RUN apt-get update && apt-get install -y libblas3 liblapack3 liblapack-dev libblas-dev libatlas-base-dev gfortran zlib1g
RUN pip install numpy
RUN pip install scipy
RUN pip install scikit-rf
RUN pip install websocket-client
```

## Docker considerations on linux-amd64

Alpine base images are very slow to build (x50) because they compile from source, so use slim instead (deb based).

`172.17.0.1` is the ip address of the host, where `session host` will be running

The target can be changed via the environment variable passed to the docker container, but defaults to:

`ws://172.17.0.1:8888/ws/calibration`

To test the service, run two websocat instances (each in a different terminal, one to observe, one to write requests)

To observe:
`websocat ws://localhost:8888/ws/calibration -`

To push a json-format request 
`websocat ws://localhost:8888/ws/calibration readfile:./test/json/oneport.json -B 999999`
or a smaller one (easier to see the request and result without scrolling)
`websocat ws://localhost:8888/ws/calibration readfile:./test/json/test.json`

## Raspberry pi build extra notes

See main README for docker info....

Note: you might see this error when building on rpi4/rpios(buster)

```
Fatal Python error: _Py_InitializeMainInterpreter: can't initialize time
PermissionError: [Errno 1] Operation not permitted
```

An issue with building `time` on rpios (`lsb_release -a` reports I am using buster) is discussed [here](https://community.home-assistant.io/t/migration-to-2021-7-fails-fatal-python-error-init-interp-main-cant-initialize-time/320648/9) and solves the problem:
```
sudo apt-key adv --keyserver keyserver.ubuntu.com --recv-keys 04EE7237B7D453EC 648ACFD622F3D138
echo "deb http://deb.debian.org/debian buster-backports main" | sudo tee -a /etc/apt/sources.list.d/buster-backports.list
sudo apt update
sudo apt install -t buster-backports libseccomp2
```

numerical libraries are required for [building scipy](https://docs.scipy.org/doc/scipy/reference/building/linux.html)
```
sudo apt-get install gcc gfortran python3-dev libopenblas-dev liblapack-dev
```
sudo apt install libblas3 liblapack3 liblapack-dev libblas-dev libatlas-base-dev gfortran zlib

An issue with building numpy on rpi (many error messages produced) is solved by adding buildtools to the Dockerfile [as described here](https://stackoverflow.com/questions/63971185/unable-to-install-numpy-on-docker-python3-7-slim-in-a-raspberry-pi)
Change
```
RUN pip install -r /var/www/requirements.txt
```
to

```
RUN apt-get update && \
    apt-get install -y \
        build-essential \
        make \
        gcc \
    && pip install -r /var/www/requirements.txt \
    && apt-get remove -y --purge make gcc build-essential \
    && apt-get autoremove -y \
    && rm -rf /var/lib/apt/lists/*
```

The build is much slower on rpi4 than desktop because the python dependencies are being compiled.

This Dockerfile now works on rpi4:
```
FROM arm32v7/python:3.7-buster
ADD calibration.py /
ADD client.py /
ENV WEBSOCKET ws://localhost:8888/ws/calibration
RUN pip install numpy
ENV DEBIAN_FRONTEND=noninteractive
RUN apt-get update && apt-get install -y libblas3 liblapack3 liblapack-dev libblas-dev libatlas-base-dev gfortran zlib1g
RUN pip install scipy
RUN pip install scikit-rf
RUN pip install websocket-client
CMD [ "python", "./client.py" ]
```
```
docker tag calibration:latest practable/calibration:arm32v7-3.7-buster-0.1
docker push practable/calibration:arm32v7-3.7-buster-0.1
```

This Dockerfile works but requires a few hours to recompile all the python libraries each time you change the contents of the python code in your app, hence the change to the two-stage build process described at the start of the document.

## Systemd

After installing docker, enable it to start on statup.
`sudo systemctl enable docker`

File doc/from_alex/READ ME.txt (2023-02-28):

Hey Tim, hope your good.

"Copper Mountain VNA" folder contains successfull measurements using a commercial VNA calibrated using the built in standards of the system.

"PocketVNA" folder contains successful measurements using the PocketVNA calibrated using the built in standards of the system.

These two should be all the data you need.

In addition to this i have also supplied a brief PT and MALAB code (almost certain you wont need but there if you want to see anything)

Lastly you will also notice that in this folder there are 4 touchstone files (DUT_1_REF TO DUT_4_REF) these are the "ideal" S-parameters of each
DUT found by connecting a commercial VNA directly across each DUT. Thought these might help establish how far off both the commercial VNA and Pocket VNA are 
from the "ideal"

Anyway hope that not too much extra waffle etc. Any issues just drop me an email.

Thanks,
Alex

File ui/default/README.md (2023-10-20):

# Pocket VNA 2-port UI

This version of the UI is a temporary fix for the pocket VNA which appears to require the measurement command to be sent twice before it returns the appropriate data.

This is the user interface for the 2-port Pocket VNA remote lab experiment found [here](https://github.com/practable/pocket-vna-two-port). This UI has been created with Vue3 + Vite build tools. 

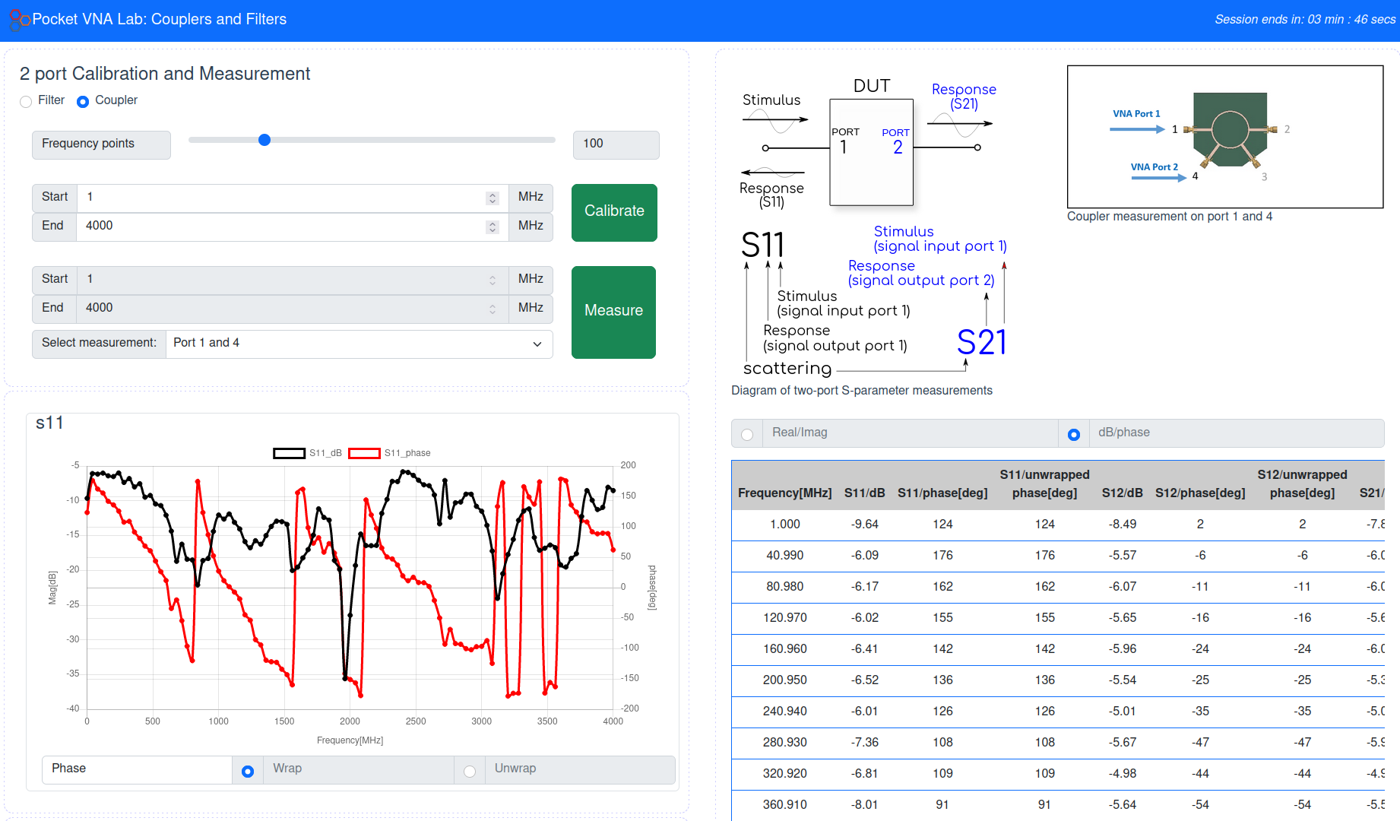
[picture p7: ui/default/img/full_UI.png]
Full UI


This is the basic version of the UI based upon the [main branch](https://github.com/dpreid/pvna-ui) of the 1-port Pocket VNA experiment UI.

## Temporary changes

In the ConnectAndDisplay.vue component changes have been made to force a second measurement.

```
data(){
    return {
        ...
        first_response: true,       //TEMPORARY for dealing with measurement issue in pocket VNA
    }
}

```

```
else if(response.cmd == 'crq'){
    this.previous_phase = null;
    console.log(response);

    //if this is the first reponse then resend the measurement command
    if(_this.first_response){

    _this.first_response = false;

    let params = {
        avg:1,
        sparam:{s11:true,s12:true,s21:true,s22:true},
        what: _this.getDUT
    }

    _this.$store.dispatch('requestRangeAfterCal', params);
    } 
    //if it is the second reponse then display data as expected
    else{
    _this.first_response = true;

    _this.$store.dispatch('setResponse', response);
    _this.$store.dispatch('setShowRequestModal', false);
    }

} 
```

## Getting data from the pocket VNA

All scattering parameters are calibrated and measured by the remote lab hardware, therefore the user interface has all scattering parameters selected by default for this 2 port system (S11, S12, S21 and S22) and this cannot be changed at the moment.

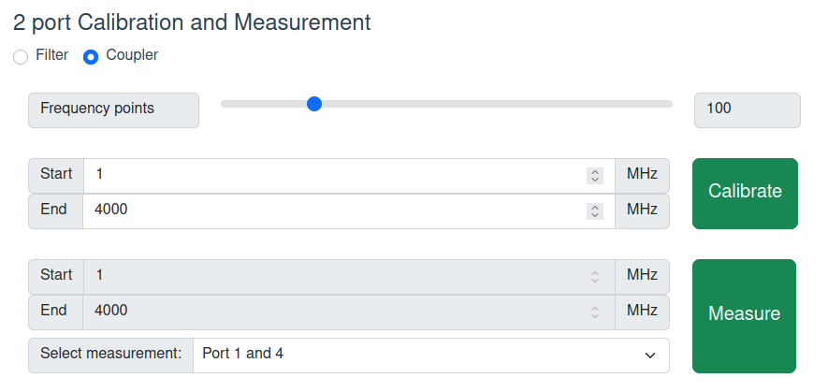
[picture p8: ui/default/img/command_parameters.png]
Command parameters


- Select the device you want to measure (filter or coupler) - an image of the device is shown in the upper right.
- Select a number of data points to collect, up to a maximum of 201. 
- Select the range of frequencies you want to measure over (max frequency 4000 MHz). 
- Click Calibrate and wait for the calibration to finish (the modal will disappear)
- Select the type of measurement you want to perform - updates the device image to show the ports that will be measured.
- Click Measure and wait for the data to be returned from the pocket VNA.

## Interacting with the data

### Graphs

Data for each scattering parameter will be displayed in a separate chart (as well as all data together in a 5th chart). To select which parameters to display (whether the magnitude in dB or the phase in deg) the user should toggle the options in the graph component.

Data (magnitude and phase) is automatically displayed for each scattering parameter in a separate chart:

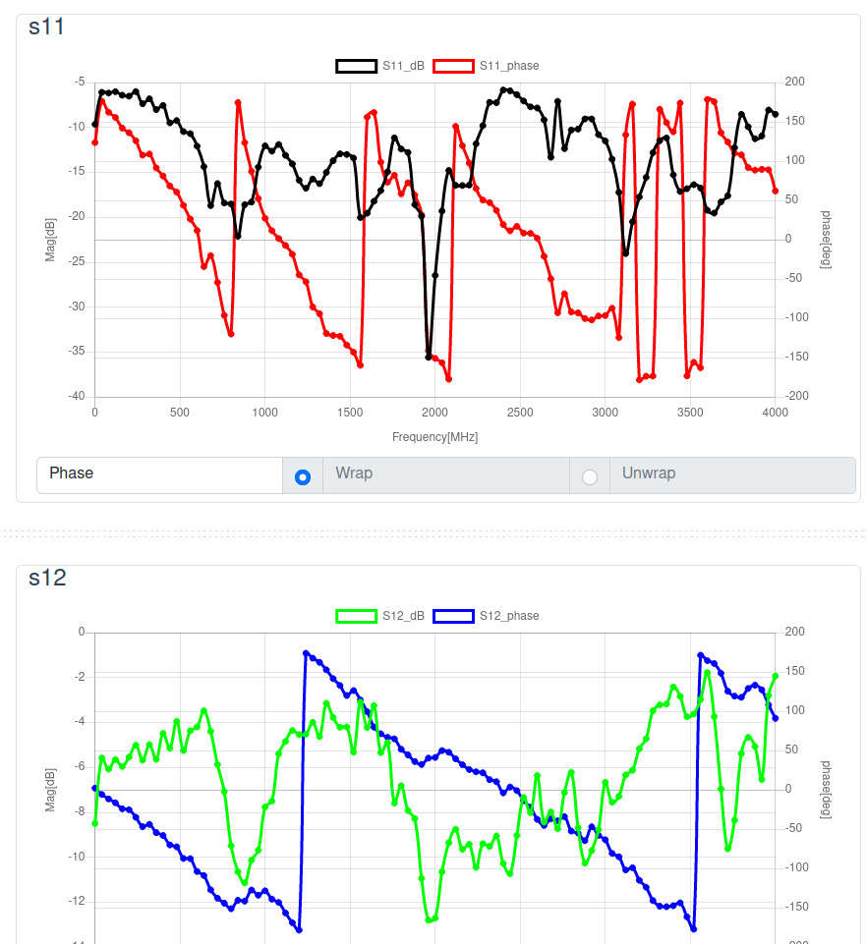
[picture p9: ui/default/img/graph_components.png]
Graph, components


You can toggle options (by clicking on the corresponding coloured rectangle, e.g. the green one below to remove that data)

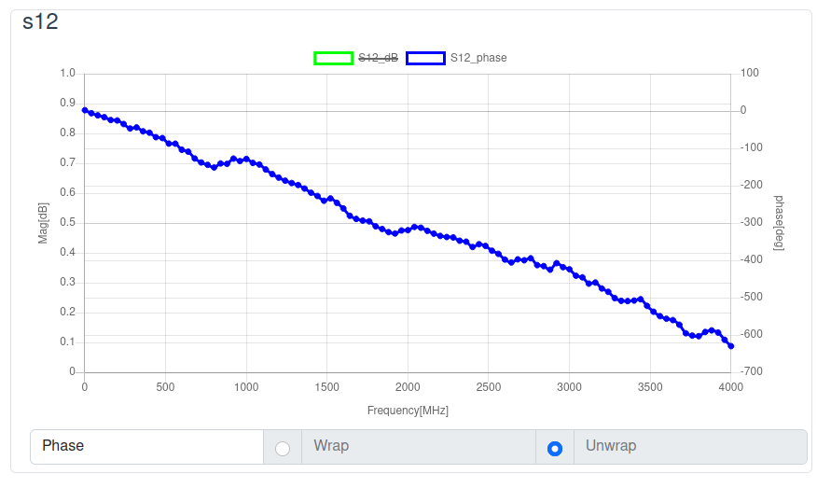
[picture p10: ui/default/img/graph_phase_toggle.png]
Graph, select data


The final chart combines all data to allow comparisons on a single chart:

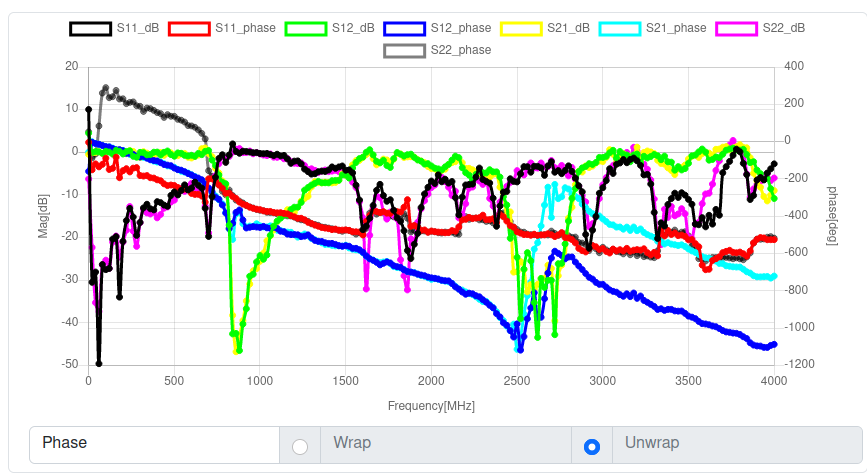
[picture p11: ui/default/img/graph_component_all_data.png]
Graph, all data


### Table

The data is also displayed in a table component providing the frequency, magnitude and phase of each data point. This can also be toggled to display in terms of the real and imaginary components instead using the selection at the top of the table.

## Downloading for external use

Although data is displayed in graphs and a table on the user interface itself, it can also be downloaded for external use. To do this, select the format of the data (real/imag or dB/phase) and the file type (csv or s2p) and then click download. This will download the file to your Downloads folder which you can then open in an appropriate program.

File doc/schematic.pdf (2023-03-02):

From | To
Switch "A"- 1 | Load
Switch "A"- 2 | Open
Switch "A"- 3 | Short
Switch "A"- 4 | DUT 4 (Port 1)
Switch "A"- 5 | PVNA 1
Switch "A"- 6 | DUT 3 (Port 1)
Switch "A"- 7 | DUT 2 (Port 1)
Switch "A"- 8 | DUT 1 (Port 1)
Switch "A"- 9 | B 9
Switch "B"- 1 | Short
Switch "B"- 2 | Open
Switch "B"- 3 | Load
Switch "B"- 4 | DUT 4 (Port 3)
Switch "B"- 5 | PVNA 2
Switch "B"- 6 | DUT 3 (Port 4)
Switch "B"- 7 | DUT 2 (Port 2)
Switch "B"- 8 | DUT 1 (Port 2)
Switch "B"- 9 | A 9

### Coupler

2

4 | 3

1

### Filter

1 | 2

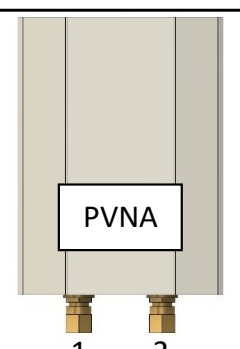
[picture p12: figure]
PVNA

## Remote Labs RF Experiment – 2 Port VNA

4
5
6

9 8 7

1 2 3

SWITCH
“A”

4
5
6

7 8 9

3 2 1

SWITCH
“B”

2

4 | 3

1

1 | 2
1 | 2

2

4 | 3

1

2

4 3

1

### DUT 1

### DUT 4

### DUT 2

### DUT 3

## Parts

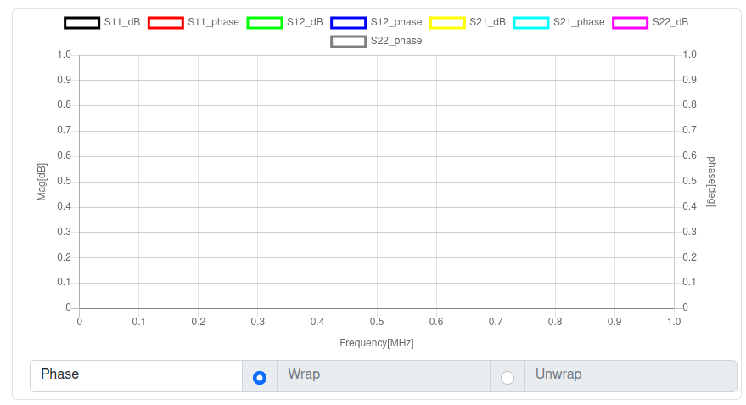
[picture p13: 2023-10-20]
ui/default/img/graph_component.png

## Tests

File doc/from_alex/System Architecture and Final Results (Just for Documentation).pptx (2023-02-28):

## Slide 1

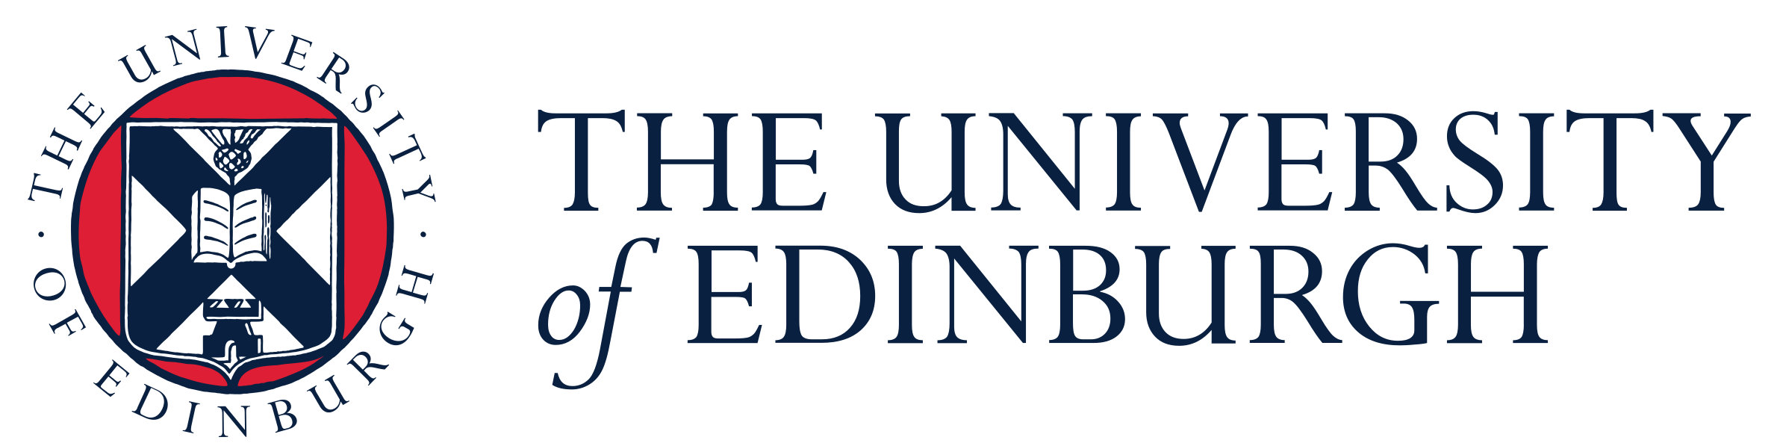
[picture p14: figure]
Download University of Edinburgh Logo in SVG Vector or PNG File Format - Logo.wine

Measuring 2 port VNA system

08-01-2023

Alexander Don
S2438345
Supervisor: Dr Symon K. Podilchak

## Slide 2

VNA Port 1

VNA Port 2

DUT 4

DUT 3

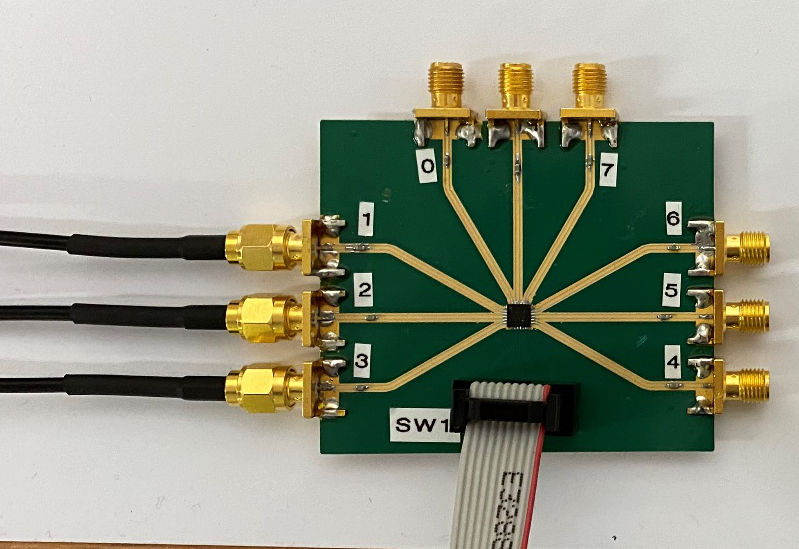
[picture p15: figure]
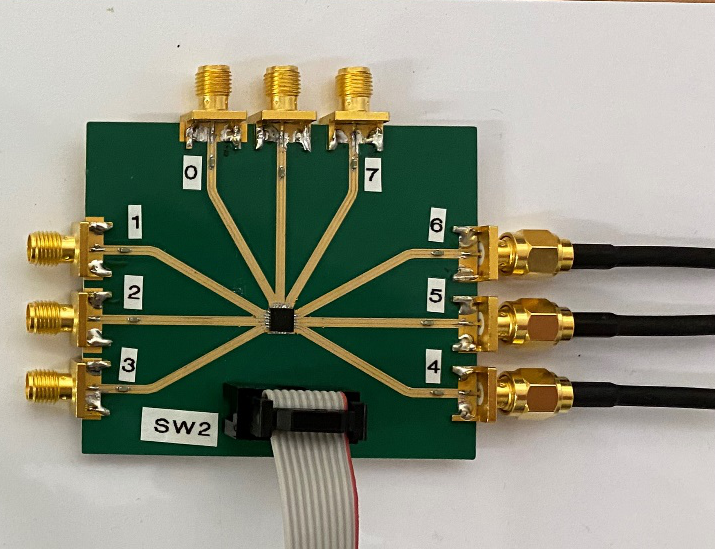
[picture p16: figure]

DUT 2

DUT 1

THRU

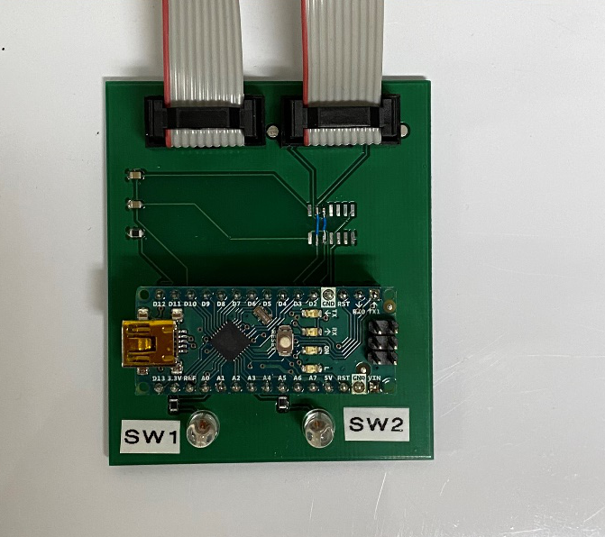
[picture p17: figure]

SHORT

OPEN

LOAD

LOAD

OPEN

SHORT

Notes: These are the port labelling's according to Max’s Code

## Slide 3

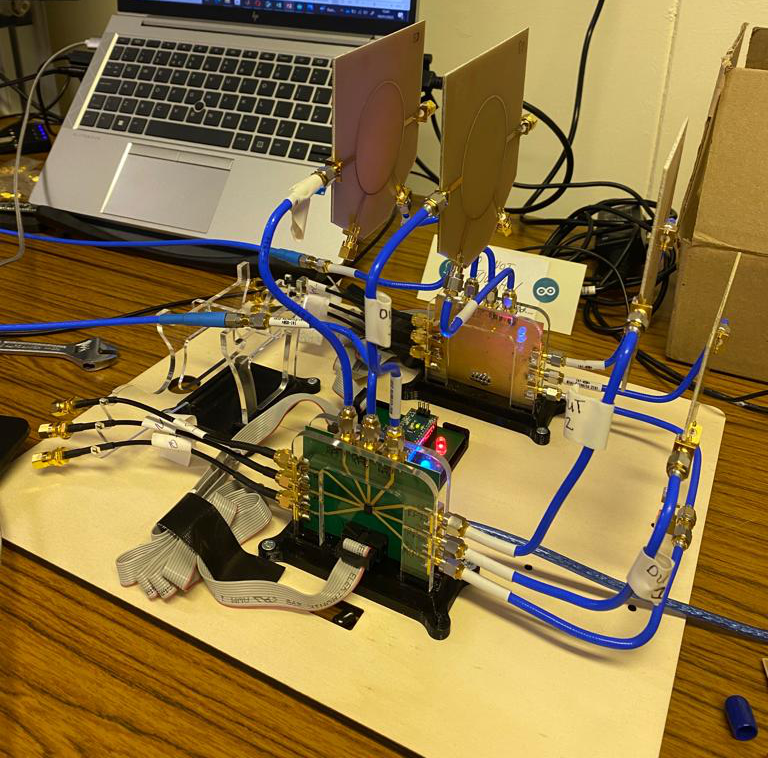
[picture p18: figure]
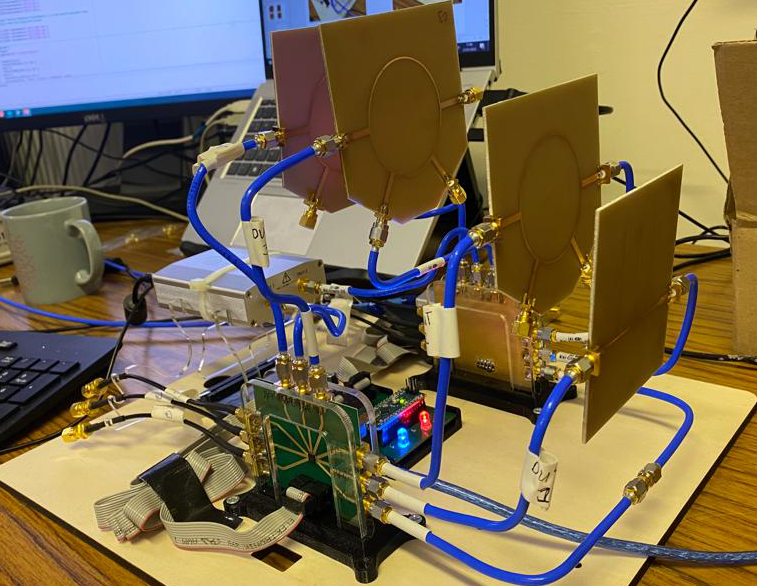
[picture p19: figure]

DUT 4

DUT 3

DUT 2

DUT 1

PocketVNA Serial Number: 2.0_1202a0971

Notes: Physical Setup of the system

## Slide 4

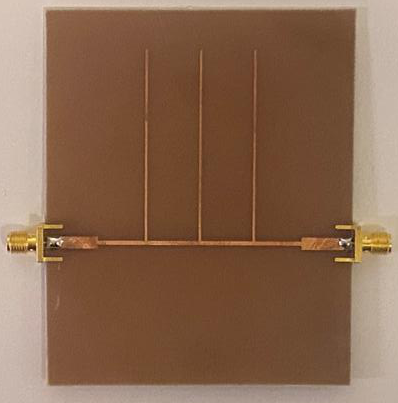
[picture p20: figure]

DUT 1

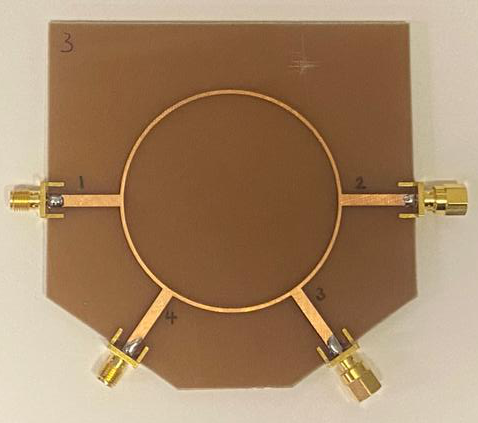
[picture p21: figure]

DUT 3

DUT 2

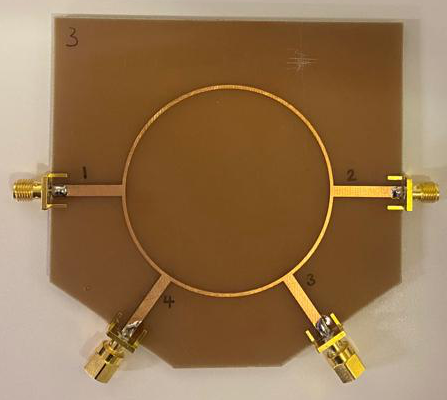
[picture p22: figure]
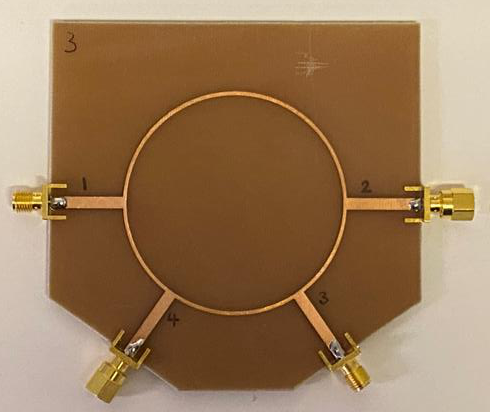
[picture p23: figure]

DUT 4

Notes: The three Devices Under Test (DUT’S)

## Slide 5

Measurement Index Sequencing

When performing the measurements ( using calibrated VNA or otherwise) the following Hex values are inputted into the serial monitor of the “nano_2p” Arduino code in the order shown.
After each reference/device is indexed then full 2-port measurement are taken of said reference/device and recorded.


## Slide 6

Measurement Labels

- Ideal Reference – The DUT was measured using the Copper Mountain VNA calibrated using its own standards using its inherent software.
- PocketVNA (PVNA) – These are the measured results using the PocketVNA after it has been calibrated using the built-in SOLT standards of the system.
- Copper Mountain VNA (CMVNA)– These are the measured results using a professional VNA (Copper Mountain VNA) after it has been calibrated using the built-in SOLT standards of the system.

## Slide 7


DUT 1

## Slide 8


DUT 2

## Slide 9


DUT 3

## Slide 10


DUT 4

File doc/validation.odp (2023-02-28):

## 2-Port Pocket VNA validation results

Practable team + RF5 team

28 Feb 2023

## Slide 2

Key:

prac: Practable Pocket VNA (automated)

pvna: manual Pocket VNA

cm: manual Copper Mountain VNA

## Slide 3


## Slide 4


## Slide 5


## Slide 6


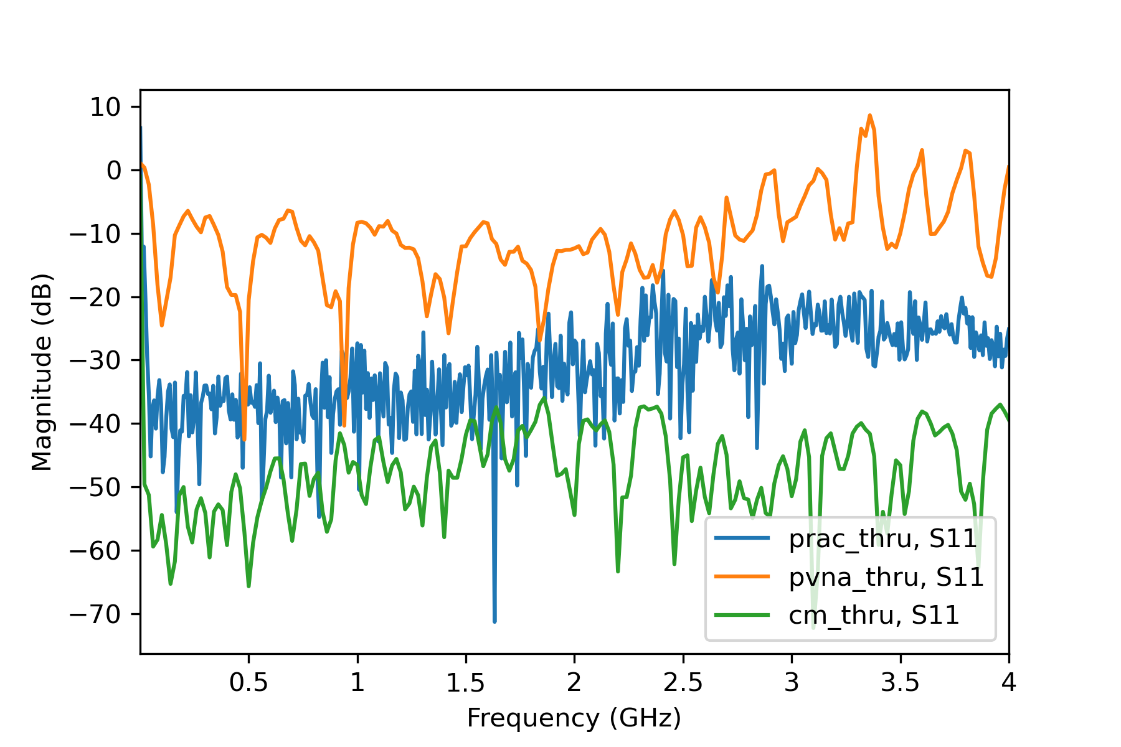
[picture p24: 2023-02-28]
img/validate-thru_db.png

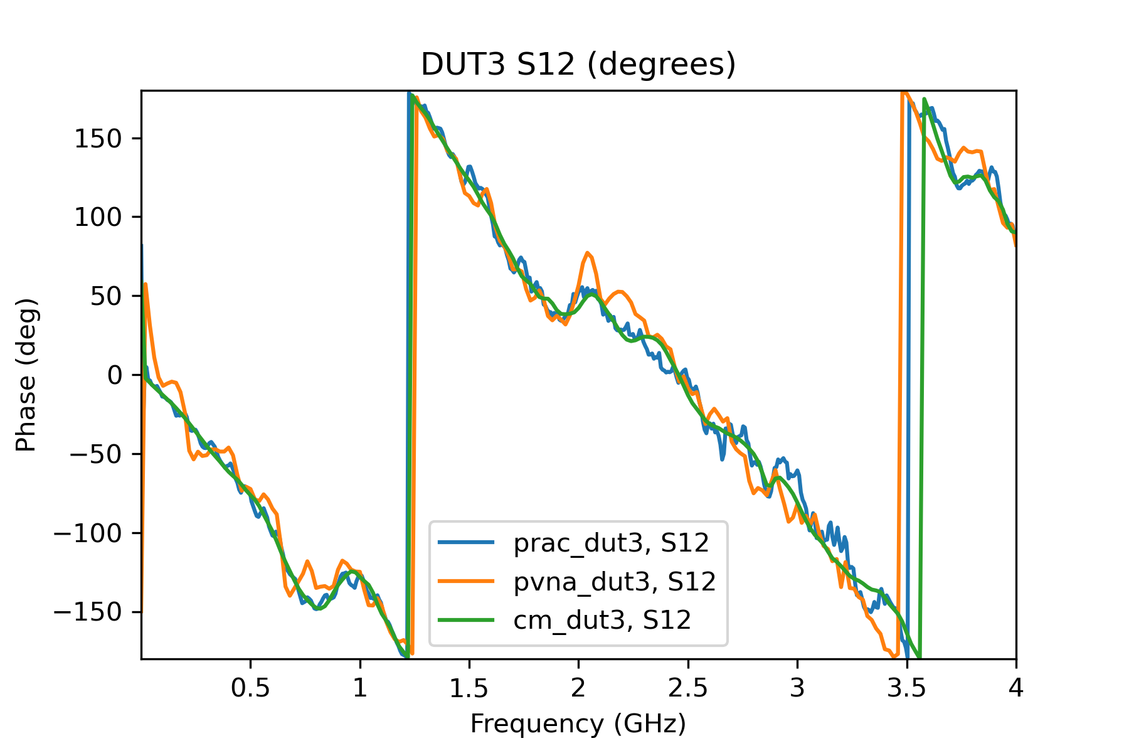
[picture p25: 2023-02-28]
img/validate-dut3_s12_deg.png

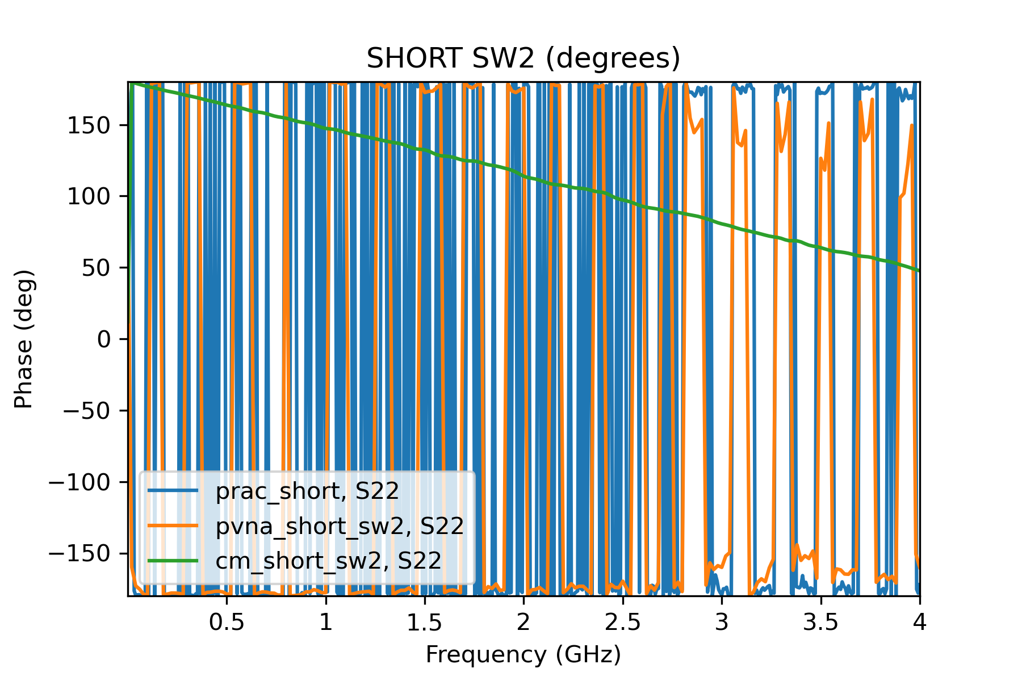
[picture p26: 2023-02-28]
img/validate-short_sw2_deg.png

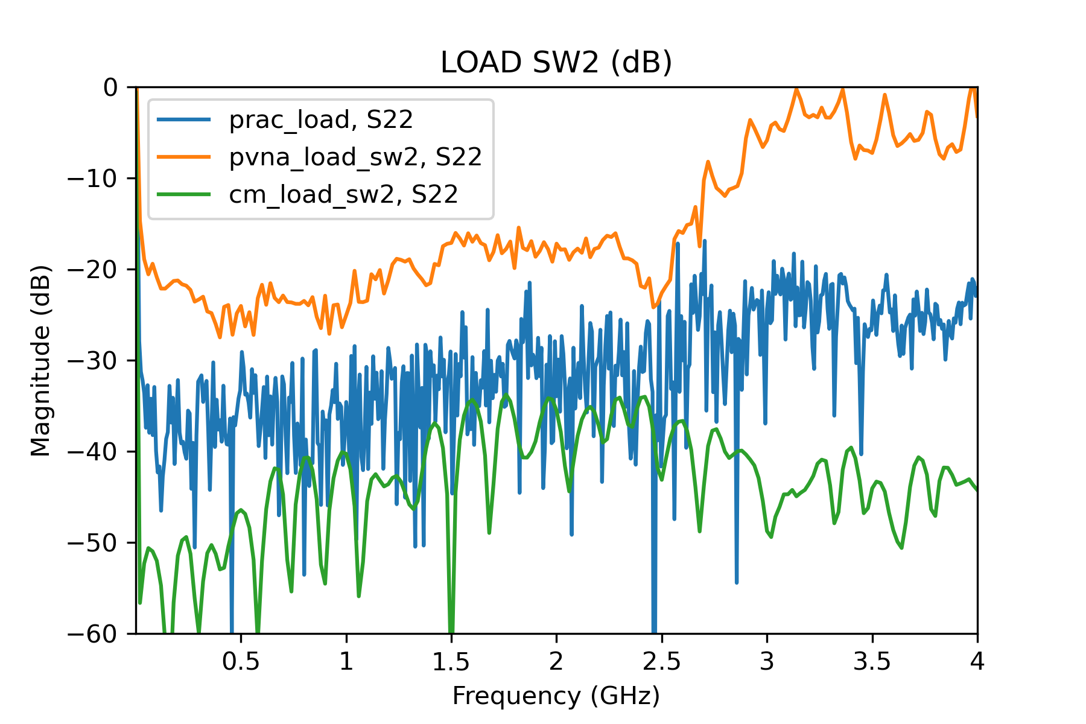
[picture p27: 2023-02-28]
img/validate-load_sw2_db.png

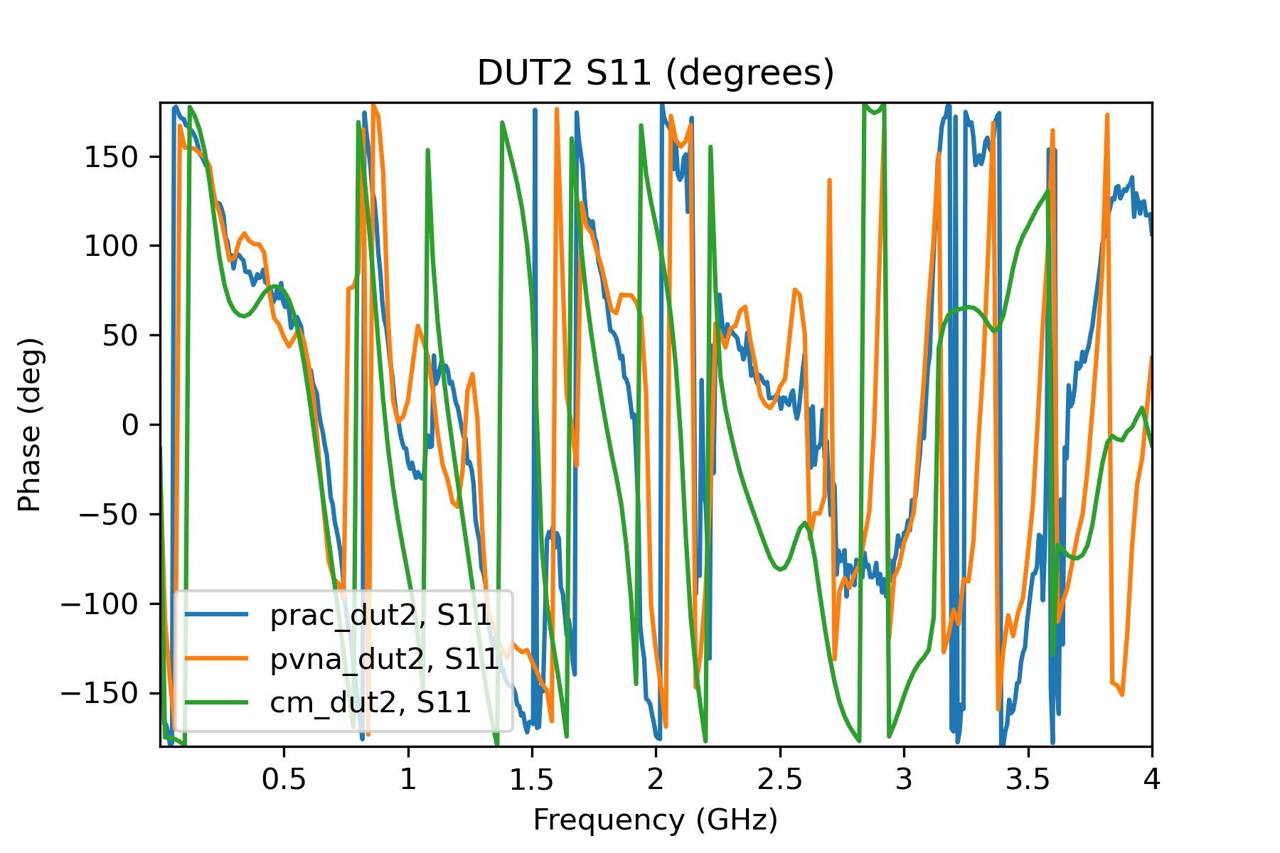
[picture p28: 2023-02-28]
img/validate-dut2_s11_deg.png

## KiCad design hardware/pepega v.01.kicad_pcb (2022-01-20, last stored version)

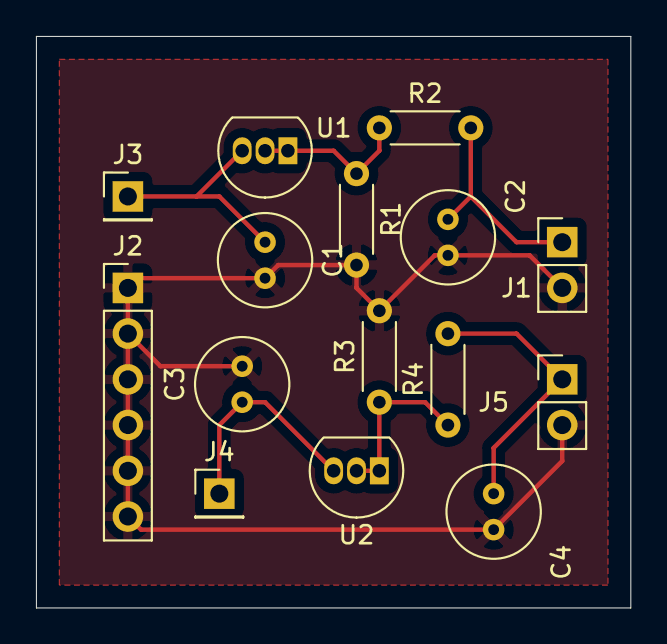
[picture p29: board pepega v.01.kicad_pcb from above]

Board: 2 copper layers, 33.0 x 31.8 mm, 15 parts (0 on the bottom side), 7 nets.

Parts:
C1, C3: 0.1 uf; C_Radial_D5.0mm_H5.0mm_P2.00mm
C2, C4: 1 uf; C_Radial_D5.0mm_H5.0mm_P2.00mm
J1, J5: Conn_01x02; PinHeader_1x02_P2.54mm_Vertical
J2: Conn_01x06_Male; PinHeader_1x06_P2.54mm_Vertical
J3, J4: Conn_01x01_Male; PinHeader_1x01_P2.54mm_Vertical
R1, R3: 100; R_Axial_DIN0204_L3.6mm_D1.6mm_P5.08mm_Horizontal
R2, R4: 470; R_Axial_DIN0204_L3.6mm_D1.6mm_P5.08mm_Horizontal
U1, U2: LM317L_TO92; TO-92_Inline

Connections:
+5F: C3.1, J4.1, U2.3
+5V: C1.1, J3.1, U1.3
GND: C1.2, C2.2, C3.2, C4.2, J1.2, J2.1, J2.2, J2.3, J2.4, J2.5, J2.6, J5.2, R1.2, R3.2
unnamed: C2.1, J1.1, R2.2
unnamed: C4.1, J5.1, R4.2
unnamed: R1.1, R2.1, U1.1, U1.2
unnamed: R3.1, R4.1, U2.1, U2.2

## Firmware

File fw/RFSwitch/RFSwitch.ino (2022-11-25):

/*
 * Remote Lab: RF Switch controller (2-port)
 * Timothy D. Drysdale
 * timothy.d.drysdale@gmail.com
 *
 * Created by Timothy D. Drysdale 25 Jan 2022 - Initial implemention based on github.com/practable/penduino
 * Modified to support 2-Port operation 10 November 2022
 *
 */

 /*********** INSTALLATION ************
  *  Requires https://github.com/khoih-prog/TimerInterrupt
  *  Install using the library manager, or manually, following the readme at the link
  */
  
 /*********** USAGE  *****************
  *  
  *  On startup, monitor at 57600 baud, you will see  {"report":"port","is":"short"}
  *  To change the port, use the commands {"set":"port","to":<port>} where port is
  *  "short", "open", "load", "dut" e.g.
  *  {"set":"port","to":"short"} 
  *  {"set":"port","to":"open"} 
  *  {"set":"port","to":"load"} 
  *  {"set":"port","to":"thru"} 
  *  {"set":"port","to":"dut1"} 
  *  {"set":"port","to":"dut2"} 
  *  {"set":"port","to":"dut3"} 
  *  {"set":"port","to":"dut4"} 
  *  You will get a confirmation message everytime you change the port setting
  *  {"report":"port","is":"short"}
  *  {"report":"port","is":"open"}
  *  {"report":"port","is":"load"}  
  *  {"report":"port","is":"dut1"}  
  *  etc  
  */


//=============================================================
// SET BOTH THESE TO FALSE BEFORE ROLLING OUT IN PRODUCTION

// report additional information (may affect performance)
bool debug = false;
bool trace = false;

//=============================================================

/********** HEADERS ******************/
#include "ArduinoJson-v6.9.1.h"
// See Timer headers below - these need a #define before them


/********** RF SWITCH ***********/
// TODO check which way round power pins are - but both are always on
// so no issue 
#define SWITCH_P1_A      8
#define SWITCH_P1_B      9
#define SWITCH_P1_C      10
#define SWITCH_P1_POWER  3
#define SWITCH_P2_A      4
#define SWITCH_P2_B      5
#define SWITCH_P2_C      6
#define SWITCH_P2_POWER  2

#define PORT_LED     15
#define POWER_LED    16

/********* RF PORTS ************/
// Check the RF output number on the RF switch 
// and see where each standard/dut is connected
// The value in the enum is zero-indexed 
// The value of the port is one-indexed
// So Port 2 in the datasheet is port 1 in the enum etc
enum port1 {
  PORT1_SHORT = 1,
  PORT1_OPEN =  2,
  PORT1_LOAD =  3,
  PORT1_THRU =  4,
  PORT1_DUT1 =  5,
  PORT1_DUT2 =  6,
  PORT1_DUT3 =  7,
  PORT1_DUT4 =  0,
};

enum port2 {
  PORT2_SHORT = 4,
  PORT2_OPEN =  5,
  PORT2_LOAD =  6,
  PORT2_THRU =  3,
  PORT2_DUT1 =  2,
  PORT2_DUT2 =  1,
  PORT2_DUT3 =  0,
  PORT2_DUT4 =  7,
};


/********* RF PORT NAME ************/
static const char name_short[] = "short";
static const char name_open[] = "open";
static const char name_load[] = "load";
static const char name_thru[] = "thru";
static const char name_dut1[] = "dut1";
static const char name_dut2[] = "dut2";
static const char name_dut3[] = "dut3";
static const char name_dut4[] = "dut4";

/*********** LED DISPLAY ***********/
#define LED_SWITCH 13

//this sets the blink code
// do not edit to suit actual RF ports
// display what port was last requested
enum blinkCode {
  BLINK_SHORT = 1,
  BLINK_OPEN = 2,
  BLINK_LOAD = 3,
  BLINK_THRU = 4,
  BLINK_DUT1 = 5,
  BLINK_DUT2 = 6,
  BLINK_DUT3 = 7,
  BLINK_DUT4 = 8,  
};

/********** TIMER *****************/
// must put #define before the include; see https://github.com/khoih-prog/TimerInterrupt/discussions/21
#define USE_TIMER_1     true

// These two includes to be included only in the .ino with setup() to avoid `Multiple Definitions` Linker Error
#include "TimerInterrupt.h"           //https://github.com/khoih-prog/TimerInterrupt
#include "ISR_Timer.h"                //https://github.com/khoih-prog/TimerInterrupt

#define TIMER_INTERVAL_MS        250L



/*********** JSON SERIAL ***********/
#define COMMAND_SIZE 128 
#define REPORT_SIZE 128 
char command[COMMAND_SIZE];
char writeBuffer[REPORT_SIZE];
StaticJsonDocument<COMMAND_SIZE> doc;


/******** OTHER GLOBAL VARIABLES ********/
bool writing;//for serial semaphore
long int count; //counter for displaying port set as blinks.
int blink; //current port state to blink according to blink enum

// pins struct represents RF switch control pin settings
struct pins {
    bool a, b, c;
};

typedef struct pins Pins;

//=============================================================
// Function Prototypes
//=============================================================

void setRFPort(int port1, int port2);
void reportRFPort(const char *name); //const since not modifying the string
void requestSerial(void);
void releaseSerial(void);
bool blinkState(long int count, int blink);
Pins getPins(int port);
void serialPrintPins(int port1, int port2);
/**
 * Defines the valid states for the state machine
 *
 */
typedef enum
{
  STATE_SHORT_BEFORE,
  STATE_SHORT_DURING,
  STATE_OPEN_BEFORE,
  STATE_OPEN_DURING,
  STATE_LOAD_BEFORE,
  STATE_LOAD_DURING,
  STATE_THRU_BEFORE,
  STATE_THRU_DURING,  
  STATE_DUT1_BEFORE,
  STATE_DUT1_DURING,
  STATE_DUT2_BEFORE,
  STATE_DUT2_DURING,
  STATE_DUT3_BEFORE,
  STATE_DUT3_DURING,
  STATE_DUT4_BEFORE,
  STATE_DUT4_DURING,  
 } StateType;

//state Machine function prototypes
//these are the functions that run whilst in each respective state.
void stateShortBefore(void);
void stateShortDuring(void);
void stateOpenBefore(void);
void stateOpenDuring(void);
void stateLoadBefore(void);
void stateLoadDuring(void);
void stateThruBefore(void);
void stateThruDuring(void);
void stateDUT1Before(void);
void stateDUT1During(void);
void stateDUT2Before(void);
void stateDUT2During(void);
void stateDUT3Before(void);
void stateDUT3During(void);
void stateDUT4Before(void);
void stateDUT4During(void);

/**
 * Type definition used to define the state
 */

typedef struct
{
  StateType State; /**< Defines the command */
  void (*func)(void); /**< Defines the function to run */
} StateMachineType;

/**
 * A table that defines the valid states of the state machine and
 * the function that should be executed for each state
 */
StateMachineType StateMachine[] =
{
  {STATE_SHORT_BEFORE, stateShortBefore},
  {STATE_SHORT_DURING, stateShortDuring},
  {STATE_OPEN_BEFORE, stateOpenBefore},
  {STATE_OPEN_DURING, stateOpenDuring}, 
  {STATE_LOAD_BEFORE, stateLoadBefore},
  {STATE_LOAD_DURING, stateLoadDuring},
  {STATE_THRU_BEFORE, stateThruBefore},
  {STATE_THRU_DURING, stateThruDuring},  
  {STATE_DUT1_BEFORE, stateDUT1Before},  
  {STATE_DUT1_DURING, stateDUT1During},  
  {STATE_DUT2_BEFORE, stateDUT2Before},  
  {STATE_DUT2_DURING, stateDUT2During},  
  {STATE_DUT3_BEFORE, stateDUT3Before},  
  {STATE_DUT3_DURING, stateDUT3During},  
  {STATE_DUT4_BEFORE, stateDUT4Before},  
  {STATE_DUT4_DURING, stateDUT4During},        
};

int numStates = 16;

/**
 * Stores the current state of the state machine
 */

StateType state = STATE_SHORT_BEFORE;    //Start with the first cal standard

//============================================================================
//           DEFINE STATE MACHINE FUNCTIONS
//
// A typical sequence uses the BEFORE state as the entry point for a given task:
//
//    STATE_<STATE>_BEFORE
//    STATE_<STATE>_DURING (repeat until finished)
//    STATE_<STATE>_AFTER
//
//  Where not currently required, these states are provided as placeholders
//  for ease of future modification.
//
//  If a change to parameters or command is needed, the typical sequence becomes 
//
//    STATE_<STATE>_BEFORE
//    STATE_<STATE>_DURING (repeat until change)
//    STATE_<STATE>_CHANGE_<SOMETHING>
//    STATE_<STATE>_DURING (repeat until finished)
//    STATE_<STATE>_AFTER
//
//  Note that you should NOT go back to BEFORE following a change -
//  reimplement any required logic from BEFORE in CHANGE_<SOMETHING>
//  so that truly one-shot setup stuff can be put in BEFORE.
// 
//  The default NEXT state is set in the first line of each state,
//  then overridden if need be.
//
//  An exception to this convention are the additional STATE_POSITION_WAITING,
//  and STATE_POSITION_READY, which are intended to let you set the PID parameters
//  before running the PID control routine, so that users can recover from setting
//  large integral coefficients, which cause an automatic stop for going out
//  of bounds before a lower PID value can be set. On entering position PID mode
//  the before state zeroes, the disk, then passes to the READY state.
//
//============================================================================

void stateShortBefore(void) {

  state = STATE_SHORT_DURING;
  setRFPort(PORT1_SHORT, PORT2_SHORT);
  reportRFPort(name_short);
  blink = BLINK_SHORT;
}

void stateOpenBefore(void) {

  state = STATE_OPEN_DURING;
  setRFPort(PORT1_OPEN, PORT2_OPEN);
  reportRFPort(name_open);
  blink = BLINK_OPEN;
}

void stateLoadBefore(void) {

  state = STATE_LOAD_DURING;
  setRFPort(PORT1_LOAD,PORT2_LOAD);
  reportRFPort(name_load);
  blink = BLINK_LOAD;
}


void stateThruBefore(void) {

  state = STATE_THRU_DURING;
  setRFPort(PORT1_THRU,PORT2_THRU);
  reportRFPort(name_thru);
  blink = BLINK_THRU;
}


void stateDUT1Before(void) {

  state = STATE_DUT1_DURING;
  setRFPort(PORT1_DUT1, PORT2_DUT1);
  reportRFPort(name_dut1);
  blink = BLINK_DUT1;
}

void stateDUT2Before(void) {

  state = STATE_DUT2_DURING;
  setRFPort(PORT1_DUT2, PORT2_DUT2);
  reportRFPort(name_dut2);
  blink = BLINK_DUT2;
}

void stateDUT3Before(void) {

  state = STATE_DUT3_DURING;
  setRFPort(PORT1_DUT3, PORT2_DUT3);
  reportRFPort(name_dut3);
  blink = BLINK_DUT3;
}

void stateDUT4Before(void) {

  state = STATE_DUT4_DURING;
  setRFPort(PORT1_DUT4, PORT2_DUT4);
  reportRFPort(name_dut4);
  blink = BLINK_DUT4;
}
void stateShortDuring(void) {

  state = STATE_SHORT_DURING;
  // do nothing

}

void stateOpenDuring(void) {

  state = STATE_OPEN_DURING;
  // do nothing
}

void stateLoadDuring(void) {

  state = STATE_LOAD_DURING;
  // do nothing
}

void stateThruDuring(void) {

  state = STATE_THRU_DURING;
  // do nothing
}

void stateDUT1During(void) {

  state = STATE_DUT1_DURING;
  // do nothing
}

void stateDUT2During(void) {

  state = STATE_DUT2_DURING;
  // do nothing
}

void stateDUT3During(void) {

  state = STATE_DUT3_DURING;
  // do nothing
}

void stateDUT4During(void) {

  state = STATE_DUT4_DURING;
  // do nothing
}



void setRFPort(int port1, int port2){

  Pins p1, p2;
  p1 = getPins(port1);
  p2 = getPins(port2);

  digitalWrite(SWITCH_P1_A, p1.a);
  digitalWrite(SWITCH_P1_B, p1.b);
  digitalWrite(SWITCH_P1_C, p1.c);
  digitalWrite(SWITCH_P2_A, p2.a);
  digitalWrite(SWITCH_P2_B, p2.b);
  digitalWrite(SWITCH_P2_C, p2.c);
  
}

void reportRFPort(const char *name){
  requestSerial();
  Serial.print("{\"report\":\"port\",\"is\":\"");
  Serial.print(name);
  Serial.println("\"}");
  releaseSerial();
  
}
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

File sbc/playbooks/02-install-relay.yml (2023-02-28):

---
- name: install relay
  hosts: pvna2:pvna2pilot
  become: yes
  gather_facts: yes
  environment:
    PATH: "/usr/local/go/bin:{{ ansible_env.PATH }}"
  tasks:

  # so we can use this playbook for update, stop the existing service
  # and ignore errors - typically only thrown if it does not exist
  - name: stop relay service
    service:
      name: relay
      state: stopped
    ignore_errors: true
     
  - name: stop relay-rules service
    service:
      name: relay-rules
      state: stopped
    ignore_errors: true    
     
  - name: build cmd/relay from practable/relay
    command: ./build.sh
    args:
      chdir: /home/pi/sources/relay/scripts/build
      
  - name: install cmd/relay to usr/local/bin
    command: cp relay /usr/local/bin
    args:
      chdir: /home/pi/sources/relay/cmd/relay
      
  - name: copy data access file
    copy: src=../autogenerated/data.access.{{ practable_label }} dest=/etc/practable/data.access

  - name: copy data token file
    copy: src=../autogenerated/data.token.{{ practable_label }} dest=/etc/practable/data.token
      
  - name: copy video access file
    copy: src=../autogenerated/video.access.{{ practable_label }} dest=/etc/practable/video.access

  - name: copy video token file
    copy: src=../autogenerated/video.token.{{ practable_label }} dest=/etc/practable/video.token
    
  - name: install relay-rules to usr/local/bin
    copy:
      src: ../files/relay-rules
      dest: /usr/local/bin/relay-rules
      owner: root
      group: root
      mode: a+x
      
  - name: Copy relay service file
    copy:
      src: ../services/relay.service
      dest: /etc/systemd/system/relay.service
      owner: root
      group: root
      
  - name: Copy relay-rules service file 
    copy:
      src: ../services/relay-rules.service
      dest: /etc/systemd/system/relay-rules.service
      owner: root
      group: root     

  - name: Just force systemd to reread configs (2.4 and above)
    ansible.builtin.systemd:
      daemon_reload: yes

  - name: start relay service
    service:
      name: relay
      state: started
      enabled: true
      
  - name: start relay-rules service
    service:
      name: relay-rules
      state: started
      enabled: true     

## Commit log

2021-10-05 Add stub for getting device info
2021-10-20 Fix README.md wording on passive devices
2022-01-20 Add cal demo
    [pepega v.01.kicad_pcb]
2022-01-25 Extract arduino code
    [pepega v.01-B_Cu.gbr, pepega v.01-B_Mask.gbr, pepega v.01-B_Paste.gbr, pepega v.01-B_SilkS.gbr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]
2022-01-25 arduino: Add LED blinks for port
2022-01-25 arduino: fix #defines/enum for switch
2022-01-25 Change calibration service result keys to lowercase
2022-01-25 Add pkg/calibration
2022-01-25 Add tests to pkg/calibration
2022-01-26 Add pkg/calibration/calibration
2022-01-26 Add TestPipeInterfaceToWs to calibration_test
2022-01-26 Add TestPipeWsToInterface to calibration_test
2022-01-26 Add TestRun to pkg/calibration
2022-01-27 Add scan to struct pkg/calibration
2022-01-27 Add calibration to pkg/middle
2022-01-27 Convert printf to log in pkg/middle
2022-02-01 Fix RFswitch message handling
    The arduino code sends blank lines occasionally, and the original
    rfswitch package was interpreting these as failed attempts at setting
    the port, causing calibration to fail. Since messages then got out of
    sequence, one blank line would cause subsequent responses to be out of
    sequence. Fixed by ignoring up to five unexpected messages after sending
    any command to the arduino, but still paying attention to whether any
    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
2022-11-10 arduino(feat): add support for two ports
2022-11-10 calibration.py(feat): add two port wip
2022-11-11 pkg(wip): calibration
2022-11-15 doc(feat): add calibration-dataset-2
2022-11-17 py(fix): twoport-dataset-2 checks in calibration.py
2022-11-17 calibration(fix): tests for twoport
2022-11-22 arduino(fix): port number off by one
2022-11-25 arduino(fix): report pins in ascending order
2022-11-25 arduino(fix): turn off debug mode
2023-02-28 all (chore): remove stale files
    [pepega v.01-B_Cu.gbr, pepega v.01-B_Mask.gbr, pepega v.01-B_Paste.gbr, pepega v.01-B_SilkS.gbr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]
2023-03-31 py (feat): add calibrate.proto
2023-03-31 py (feat): test protoc server
    gRPC server implemented for two port calibration, and tested with python
    client using data from CopperMountainVNA - using calibrated data, and
    checking that the results are the same before and after calibration
    (because the error correction will be basically zero). Does not protect
    against an echo server implementation passing test, but for now we don't
    have a ready-made dataset with the raw DUT values to use.
2023-11-28 pkg/calibrate (feat): add test
2023-12-01 pkg/calibration (chore): remove this stale package
2023-12-11 updated to have ports that can be synced for the calibration and new placeholder command ready for firmware update for response when scanning
2023-12-13 have updated components to separate out the calibration parameters into a separate component. Next, need to add a new tab where the parameters are set
2023-12-14 new tab for setting parameters before calibration - not tested with data connection
2023-12-15 middle (feat): add stepwise calibration
2023-12-20 sbc (fix): arduino-cli path
2024-01-09 pkg/middle (fix): remove CalQuery case from Handle()
2024-01-16 added an error modal and message if the calibration process is not complete
2024-01-16 reset booleans for parameters set, calibrated etc
2024-01-16 removed test calibrate button
2024-01-22 ui(update): images of cal standards now have a short blue cable connected
